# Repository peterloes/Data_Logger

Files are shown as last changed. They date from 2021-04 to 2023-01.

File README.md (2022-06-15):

# Next generation of data logger for varied range support of sensors.

A standalone platform to get environmental impact around organisms (animals).
Enable long-term observations of different selectable sensors (I2C Interfaces).
Two pulse counters are included to get lightbarrier activity.

Authors: Loës P., Kempenaers B.(2021) 

## Main advantages against other data logger:

- Available sensors can be freely combined as required.(Firmware adaption)
- Daily regular synchronisation from date and time with DCF77 radio clock receiver.(Firmware adaption)
- Long battery life with lithium battery. (max.17V)
- SD Card includes configuration file.
- Activation times for sensors (x5) to collect data.

## Hardware Design (first draft) supported:

The following firmware is not reviewed.

- Sensirion: Humidity and Temperature Sensor SHT3x-DIS
- Sensirion: CO₂, Humidity and Temperature Sensor SCD30
- Vishay: Fully Integrated Proximity and Ambient Light Sensor with Infrared Emitter VCNL4040
- Pulse Counter     	 

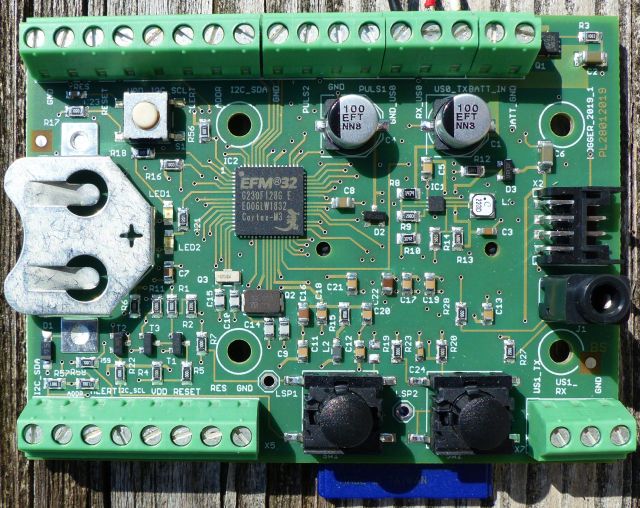
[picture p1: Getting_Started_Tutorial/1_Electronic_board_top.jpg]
My image


Board Dimensions: 80mm x 60mm

Raw data on SD Card:

https://github.com/peterloes/Data_Logger/blob/main/Getting_Started_Tutorial/4_rawdata_BOX0999.TXT

Configuration data on SD Card:

https://github.com/peterloes/Data_Logger/blob/main/Software/CONFIG.TXT

Schematics:

https://github.com/peterloes/Data_Logger/blob/main/Schematics/Logger.sch.pdf

Housing:

https://github.com/peterloes/Data_Logger/blob/main/Getting_Started_Tutorial/11_Electronic_housing.jpg

## Hyperterminal Screens

Shows SHT31X-D (0x45) and SHT31X-D (0x45)

https://github.com/peterloes/Data_Logger/blob/main/Getting_Started_Tutorial/3_Hyperterminal_3.jpg

https://github.com/peterloes/Data_Logger/blob/main/Getting_Started_Tutorial/3_Hyperterminal_4.jpg

In operation with Interval (configuration.txt) : 3,2V@0,54mA

Shows Vishay VCNL4040 (0x60) and SHT31X-D (0x45)

https://github.com/peterloes/Data_Logger/blob/main/Getting_Started_Tutorial/3_Hyperterminal_5.jpg

Shows Vishay VCNL4040 (0x60) and Sensirion SCD30 CO2 (0x61)

https://github.com/peterloes/Data_Logger/blob/main/Getting_Started_Tutorial/3_Hyperterminal_6.jpg

## Board Power

 - Lithium battery  17V/300mA(maximum) e.g. 12,8V 7,5Ah 96Wh 
 - LS14250 Primary Lithium-Thionyl chloride    3.6V/1200mAh 

Sensors can powered by VBATT_1(3.3V), VBATT_2(3V):

 - Sensirion: Humidity and Temperature Sensor SHT3x-DIS:        600µA@3,3V

 - Sensirion: CO₂, Humidity and Temperature Sensor SCD30:     max.75mA@3,3V 

 - Vishay: Proximity Sensor and Ambient Light Sensor VCNL 4040: 300µA@2,5V

   Similar Software(SensorMon.c): https://github.com/peterloes/HRD_SENSOR

Optional components:

https://github.com/peterloes/Clock_receiver_RFID-MS_MOMO_TAMDL

https://github.com/peterloes/Booter_RFID-MS_MOMO_TAMDL

Outlook:

The Data Logger can feature two arrays with different sensors over 25 meters. (sensor-array x 2)

C is the Greenest Programming Language

To achieve its power and energy-efficiency features, EFM32 products utilize ultralow active and idle power,
fast wakeup and processing times, and most important, the ability to intelligently interact with peripherals
and sensors autonomously without waking up the CPU and consuming more power.

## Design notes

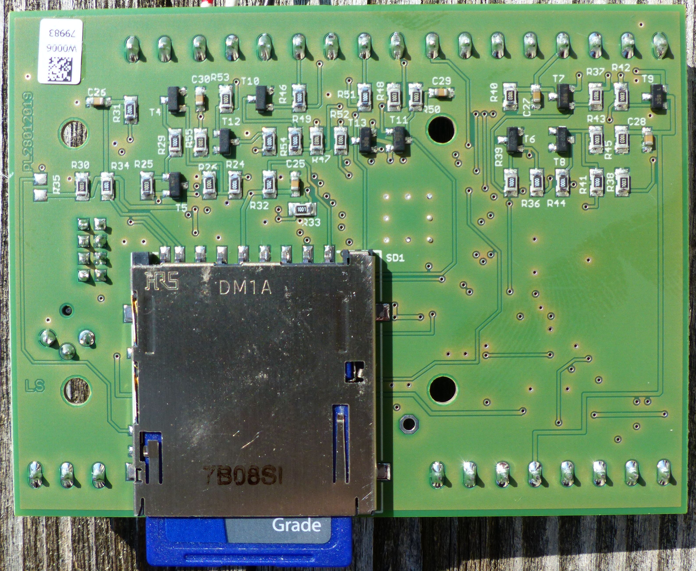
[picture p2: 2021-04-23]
Getting_Started_Tutorial/2_Electronic_board_bottom.jpg

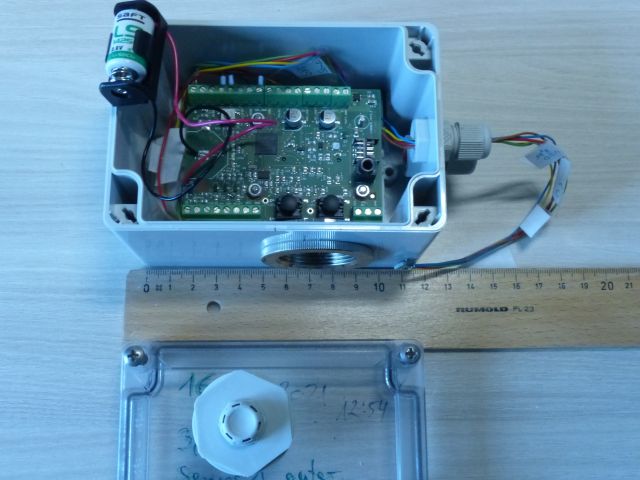
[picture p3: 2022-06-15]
Getting_Started_Tutorial/11_Electronic_housing.jpg

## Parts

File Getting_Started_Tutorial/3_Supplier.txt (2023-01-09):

Lithium Ionen rechargeable battery pack Art.Nr. 60.16294 Panasonic NCR 18650GA 4S2P
14,4Volt 6900mAh inklusive SMBus Kabel je. 150mm 

DYNAMIS Batterien GmbH
Josef Pfeil

Brühlstraße 15  D- 78465 Dettingen / Konstanz
Tel. +49 (0) 75 33/93 669-15
mailto:josef.pfeil@dynamis-batterien.de
www.dynamis-batterien.de

Supplier of all Electronic Boards

Top-Print Electronic GmbH
Oskar Schmid

Rosenheimer Landstr. 129a
85521 Ottobrunn
Germany
Tel.: +49-89-60668047
Fax: +49-89-60668049
mailto: info@top-print.eu
https://www.leiterplatten-muenchen.de/

FTDI Chip cable (3.5mm Audio Jack to USB)
TTL-232R-3V3-AJ

https://de.rs-online.com/
Battery holder with cable
RS PRO Batteriehalter mit Drahtanschluss 1/2 AA Batterien
RS Best.-Nr.: 185-4655

Docklight RS232 Terminal / RS232 Monitor
https://docklight.de/information/

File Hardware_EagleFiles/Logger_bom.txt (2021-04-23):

Stückliste exportiert aus C:/MPIO/TECHNIK/HARDWARE/EAGLE_FILES/Logger_2019/Logger_2019_1.sch am 21.04.2021 15:29

Part  Value                   Device                  Package                Description                                                    MF MPN     OC_FARNELL OC_NEWARK PACKAGE  SUPPLIER         
BH1   KEYSTONE_CELL_CLIP 3082 3082                    3082                                                                                                                                            
C1    100µF/25V               CPOL-EUE                PANASONIC_E            POLARIZED CAPACITOR, European symbol                                                                                     
C2    10µF/25V                C-EUC1206               C1206                  CAPACITOR, European symbol                                                                                               
C3    22µF/10V                C-EUC0603               C0603                  CAPACITOR, European symbol                                                                                               
C4    100µF/25V               CPOL-EUE                PANASONIC_E            POLARIZED CAPACITOR, European symbol                                                                                     
C5    100nF/16V               C-EUC0805               C0805                  CAPACITOR, European symbol                                                                                               
C6    10µ/25V                 C-EUC1206               C1206                  CAPACITOR, European symbol                                                                                               
C7    100n                    C_SMD0805               0805                                                                                                                                            
C8    1u                      C_SMD0805               0805                                                                                                                                            
C9    12p                     C_SMD0805               0805                                                                                                                                            
C10   18p                     C_SMD0805               0805                                                                                                                                            
C11   100n                    C_SMD0805               0805                                                                                                                                            
C12   100n                    C_SMD0805               0805                                                                                                                                            
C13   100n                    C_SMD0805               0805                                                                                                                                            
C14   12p                     C_SMD0805               0805                                                                                                                                            
C15   18p                     C_SMD0805               0805                                                                                                                                            
C16   10µ                     C_SMD0805               0805                                                                                                                                            
C17   100n                    C_SMD0805               0805                                                                                                                                            
C18   100n                    C_SMD0805               0805                                                                                                                                            
C19   100n                    C_SMD0805               0805                                                                                                                                            
C20   100n                    C_SMD0805               0805                                                                                                                                            
C21   100n                    C_SMD0805               0805                                                                                                                                            
C22   10µ                     C_SMD0805               0805                                                                                                                                            
C23   10n                     C-EUC0603               C0603                  CAPACITOR, European symbol                                                                                               
C24   10n                     C-EUC0603K              C0603K                 CAPACITOR, European symbol                                                                                               
C25   100nF                   C-EUC0603               C0603                  CAPACITOR, European symbol                                                                                               
C26   100nF                   C-EUC0603               C0603                  CAPACITOR, European symbol                                                                                               
C27   100nF                   C-EUC0603               C0603                  CAPACITOR, European symbol                                                                                               
C28   100nF                   C-EUC0603               C0603                  CAPACITOR, European symbol                                                                                               
C29   100nF                   C-EUC0603               C0603                  CAPACITOR, European symbol                                                                                               
C30   100nF                   C-EUC0603               C0603                  CAPACITOR, European symbol                                                                                               
D1    RSX101M-30              DIODE-SOD123            SOD123                 DIODE                                                                                                                    
D2    BAT54C                  D2A_SOT23               SOT-23$1               Dual DIODE                                                                                                               
D3    BAT54C                  D2A_SOT23               SOT-23$1               Dual DIODE                                                                                                               
IC1   TPS62125                TPS62125                DSG_PWSO-N8_EXP                                                                                                                                 
IC2   EFM32G230F128           EFM32G230F128           QFN64                  EFM32G230F128 Gecko Microcontroller in 9mm x 9mm QFN64 package                                                           
J1    LUMBERG1502_01          LUMBERG1502_01          LUMBERG1502_01                                                                                                                                  
L1    LPS3008/22µH            LPS3008                 LPS3008                                                                                                                                         
L2    BLM21B102S              WE-CBF-7427920_0805     0805                   SMD EMI Suppression Ferrite Beads WE-CBF                          7427920 1635707    08P2358   IND-0805 Wuerth Elektronik
LED1  SML-H12U8TT86           LEDCHIPLED_0805         CHIPLED_0805           LED                                                                                                                      
LED2  SML-H12Y8TT86           LEDCHIPLED_0805         CHIPLED_0805           LED                                                                                                                      
LSP1  (n.b.)SE13              SE13                    SE13                   SOLDER PAD E1542,  drill 1,3mm, distributor Buerklin, 07F815                                                             
LSP2  (n.b.)SE13              SE13                    SE13                   SOLDER PAD E1542,  drill 1,3mm, distributor Buerklin, 07F815                                                             
PASS1 ROUND_1MM1.5            ROUND_1MM1.5            ROUND2_1.5MM                                                                                                                                    
PASS2 ROUND_1MM1.5            ROUND_1MM1.5            ROUND2_1.5MM                                                                                                                                    
Q1    SI7121DN                TRANSISTOR-FET_SI7113DN TRANSISTOR-FET_1212-8S                                                                                                                          
Q2    NX5032GA/32MHz/8pF      CRYSTAL2P5.0X3.2        CRYSTAL2P5.0X3.2       Quarz Crystal                                                                                                            
Q3    CM7V, 32768Hz/12.5pF    CRYSTAL2P               CRYSTAL2P3.2X1.5       Quarz Crystal                                                                                                            
R1    100                     R-EU_R0805              R0805                  RESISTOR, European symbol                                                                                                
R2    100K                    R-EU_R0805              R0805                  RESISTOR, European symbol                                                                                                
R3    100k                    R-EU_R0805              R0805                  RESISTOR, European symbol                                                                                                
R4    100K                    R-EU_R0805              R0805                  RESISTOR, European symbol                                                                                                
R5    100                     R-EU_R0805              R0805                  RESISTOR, European symbol                                                                                                
R6    100K                    R-EU_R0805              R0805                  RESISTOR, European symbol                                                                                                
R7    100                     R-EU_R0805              R0805                  RESISTOR, European symbol                                                                                                
R8    1M47                    R-EU_R0805              R0805                  RESISTOR, European symbol                                                                                                
R9    200K                    R-EU_R0805              R0805                  RESISTOR, European symbol                                                                                                
R10   30K9                    R-EU_R0805              R0805                  RESISTOR, European symbol                                                                                                
R11   100K                    R-EU_R0805              R0805                  RESISTOR, European symbol                                                                                                
R12   100K                    R-EU_R0805              R0805                  RESISTOR, European symbol                                                                                                
R13   2M                      R-EU_R0805              R0805                  RESISTOR, European symbol                                                                                                
R14   560K                    R-EU_R0805              R0805                  RESISTOR, European symbol                                                                                                
R15   1                       R-EU_R0805              R0805                  RESISTOR, European symbol                                                                                                
R16   100K                    R-EU_R0805              R0805                  RESISTOR, European symbol                                                                                                
R17   100                     R-EU_R0805              R0805                  RESISTOR, European symbol                                                                                                
R18   1K2                     R-EU_R0805              R0805                  RESISTOR, European symbol                                                                                                
R19   (n.b.)100K/*10nF*/      R-EU_R0805              R0805                  RESISTOR, European symbol                                                                                                
R20   100K                    R-EU_R0805              R0805                  RESISTOR, European symbol                                                                                                
R21   1K2                     R-EU_R0805              R0805                  RESISTOR, European symbol                                                                                                
R22   100                     R-EU_R0805              R0805                  RESISTOR, European symbol                                                                                                
R23   100                     R-EU_R0805              R0805                  RESISTOR, European symbol                                                                                                
R24   100                     R-EU_R0805              R0805                  RESISTOR, European symbol                                                                                                
R25   100K                    R-EU_R0805              R0805                  RESISTOR, European symbol                                                                                                
R26   100K                    R-EU_R0805              R0805                  RESISTOR, European symbol                                                                                                
R27   10K                     R-EU_R0805              R0805                  RESISTOR, European symbol                                                                                                
R28   10K                     R-EU_R0805              R0805                  RESISTOR, European symbol                                                                                                
R29   100                     R-EU_R0805              R0805                  RESISTOR, European symbol                                                                                                
R30   100K                    R-EU_R0805              R0805                  RESISTOR, European symbol                                                                                                
R31   10K                     R-EU_R0805              R0805                  RESISTOR, European symbol                                                                                                
R32   10K                     R-EU_R0805              R0805                  RESISTOR, European symbol                                                                                                
R33   1K                      R-EU_R0805              R0805                  RESISTOR, European symbol                                                                                                
R34   1K                      R-EU_R0805              R0805                  RESISTOR, European symbol                                                                                                
R35   (n.b.)10K               R-EU_R0805              R0805                  RESISTOR, European symbol                                                                                                
R36   100                     R-EU_R0805              R0805                  RESISTOR, European symbol                                                                                                
R37   100K                    R-EU_R0805              R0805                  RESISTOR, European symbol                                                                                                
R38   100K                    R-EU_R0805              R0805                  RESISTOR, European symbol                                                                                                
R39   100                     R-EU_R0805              R0805                  RESISTOR, European symbol                                                                                                
R40   100K                    R-EU_R0805              R0805                  RESISTOR, European symbol                                                                                                
R41   100                     R-EU_R0805              R0805                  RESISTOR, European symbol                                                                                                
R42   100K                    R-EU_R0805              R0805                  RESISTOR, European symbol                                                                                                
R43   100K                    R-EU_R0805              R0805                  RESISTOR, European symbol                                                                                                
R44   100                     R-EU_R0805              R0805                  RESISTOR, European symbol                                                                                                
R45   100K                    R-EU_R0805              R0805                  RESISTOR, European symbol                                                                                                
R46   100                     R-EU_R0805              R0805                  RESISTOR, European symbol                                                                                                
R47   100K                    R-EU_R0805              R0805                  RESISTOR, European symbol                                                                                                
R48   100K                    R-EU_R0805              R0805                  RESISTOR, European symbol                                                                                                
R49   100                     R-EU_R0805              R0805                  RESISTOR, European symbol                                                                                                
R50   100K                    R-EU_R0805              R0805                  RESISTOR, European symbol                                                                                                
R51   100                     R-EU_R0805              R0805                  RESISTOR, European symbol                                                                                                
R52   100K                    R-EU_R0805              R0805                  RESISTOR, European symbol                                                                                                
R53   100K                    R-EU_R0805              R0805                  RESISTOR, European symbol                                                                                                
R54   100                     R-EU_R0805              R0805                  RESISTOR, European symbol                                                                                                
R55   100K                    R-EU_R0805              R0805                  RESISTOR, European symbol                                                                                                
R56   1K                      R-EU_R0805              R0805                  RESISTOR, European symbol                                                                                                
R57   1K                      R-EU_R0805              R0805                  RESISTOR, European symbol                                                                                                
R58   1K                      R-EU_R0805              R0805                  RESISTOR, European symbol                                                                                                
R59   1K                      R-EU_R0805              R0805                  RESISTOR, European symbol                                                                                                
S1    SWPB_B3S1000            DTSM-6                  DTSM-6                                                                                                                                          
SD1   DM1AA-SF-PEJ            DM1AA-SF-PEJ            DM1AA-SF-PEJ                                                                                                                                    
SW1   5GSH935                 5GSH935                 MULTIMEC_5GSH935                                                                                                                                
SW2   5GSH935                 5GSH935                 MULTIMEC_5GSH935                                                                                                                                
T1    2N7002                  NMOSSOT23               SOT-23                 MOS FET                                                                   unknown    unknown                             
T2    FDN358P                 ZETEX_PMOSSOT23         ZETEX_SOT-23           MOS FET                                                                                                                  
T3    2N7002                  NMOSSOT23               SOT-23                 MOS FET                                                                   unknown    unknown                             
T4    2N7002                  ZETEX_NMOSSOT23         ZETEX_SOT-23           MOS FET                                                                                                                  
T5    FDN358P                 ZETEX_PMOSSOT23         ZETEX_SOT-23           MOS FET                                                                                                                  
T6    2N7002                  ZETEX_NMOSSOT23         ZETEX_SOT-23           MOS FET                                                                                                                  
T7    FDN358P                 ZETEX_PMOSSOT23         ZETEX_SOT-23           MOS FET                                                                                                                  
T8    2N7002                  ZETEX_NMOSSOT23         ZETEX_SOT-23           MOS FET                                                                                                                  
T9    FDN358P                 ZETEX_PMOSSOT23         ZETEX_SOT-23           MOS FET                                                                                                                  
T10   2N7002                  ZETEX_NMOSSOT23         ZETEX_SOT-23           MOS FET                                                                                                                  
T11   FDN358P                 ZETEX_PMOSSOT23         ZETEX_SOT-23           MOS FET                                                                                                                  
T12   2N7002                  ZETEX_NMOSSOT23         ZETEX_SOT-23           MOS FET                                                                                                                  
T13   FDN358P                 ZETEX_PMOSSOT23         ZETEX_SOT-23           MOS FET                                                                                                                  
X1    MKDS1/2-3,81            MKDS1/2-3,81            2POL381                MKDS 1/2-3,81 - Order No. 1727010 (RS-Online - 101-5384)                                                                 
X2    DF11_8DP_2DS            DP11_8DP_2DS            DP11_8DP-2DS                                                                                                                                    
X3    MKDS1/3-3,81            MKDS1/3-3,81            3POL381                MKDS 1/3-3,81 - Order No. 1727023 (RS-Online - 101-5390)                                                                 
X4    MKDS1/8-3,81            MKDS1/8-3,81            8POL381                MKDS 1/8-3,81 - Order No. 1727078                                                                                        
X5    MKDS1/8-3,81            MKDS1/8-3,81            8POL381                MKDS 1/8-3,81 - Order No. 1727078                                                                                        
X6    MKDS1/4-3,81            MKDS1/4-3,81            4POL381                MKDS 1/4-3,81 - Order No. 1727036                                                                                        
X7    MKDS1/3-3,81            MKDS1/3-3,81            3POL381                MKDS 1/3-3,81 - Order No. 1727023 (RS-Online - 101-5390)

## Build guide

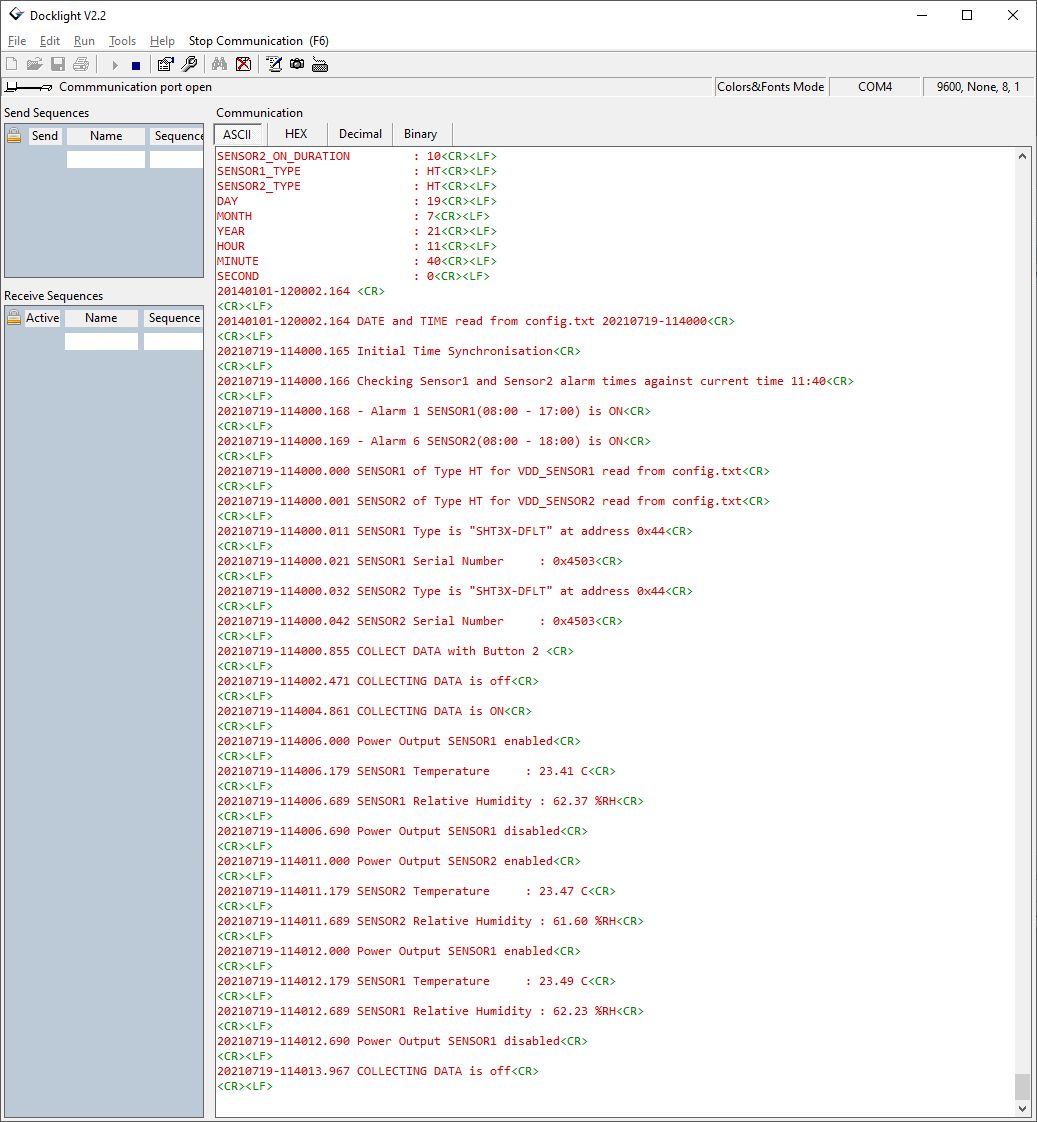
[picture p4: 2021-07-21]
Getting_Started_Tutorial/3_Hyperterminal_4.jpg

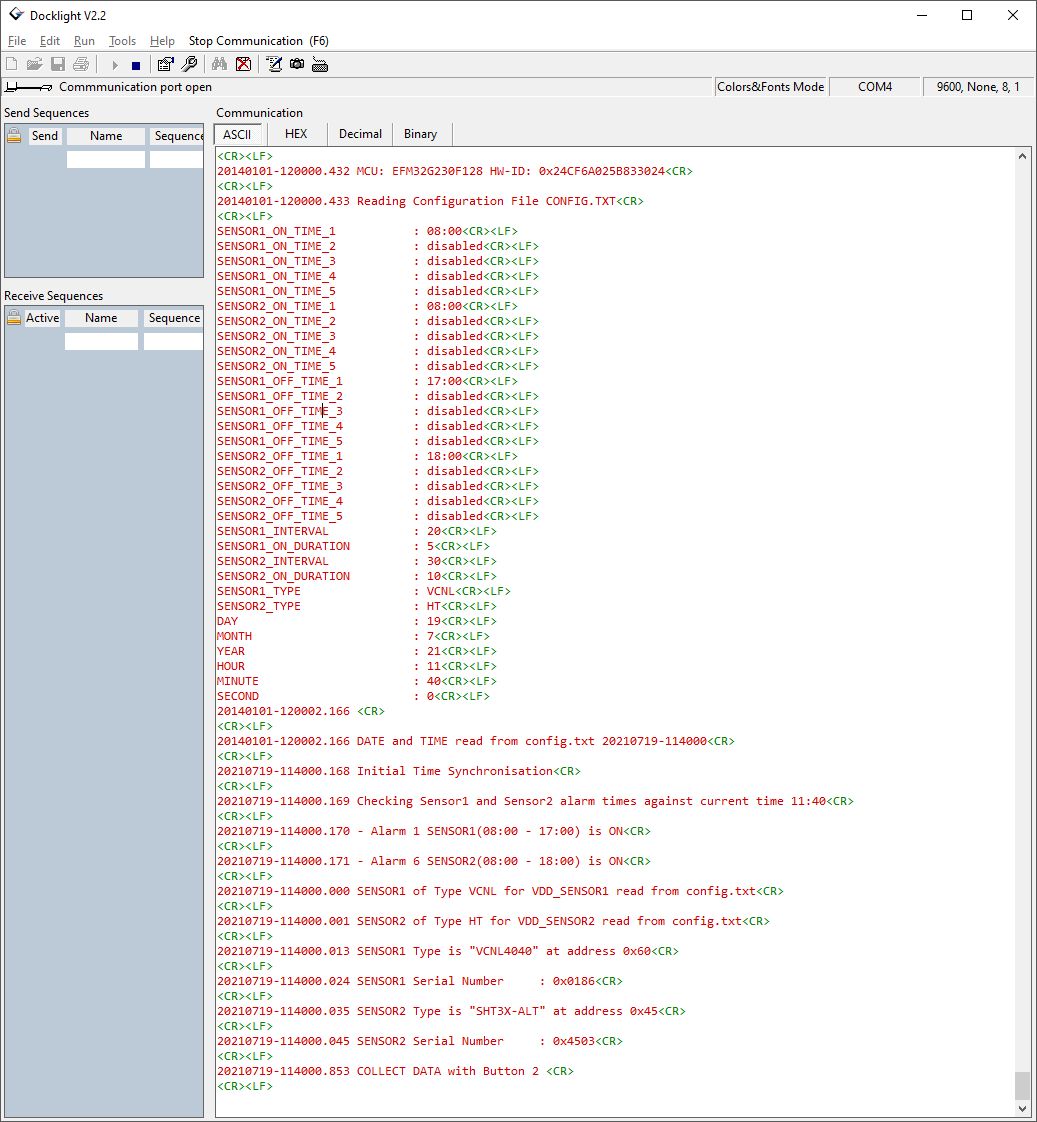
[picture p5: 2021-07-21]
Getting_Started_Tutorial/3_Hyperterminal_5.jpg

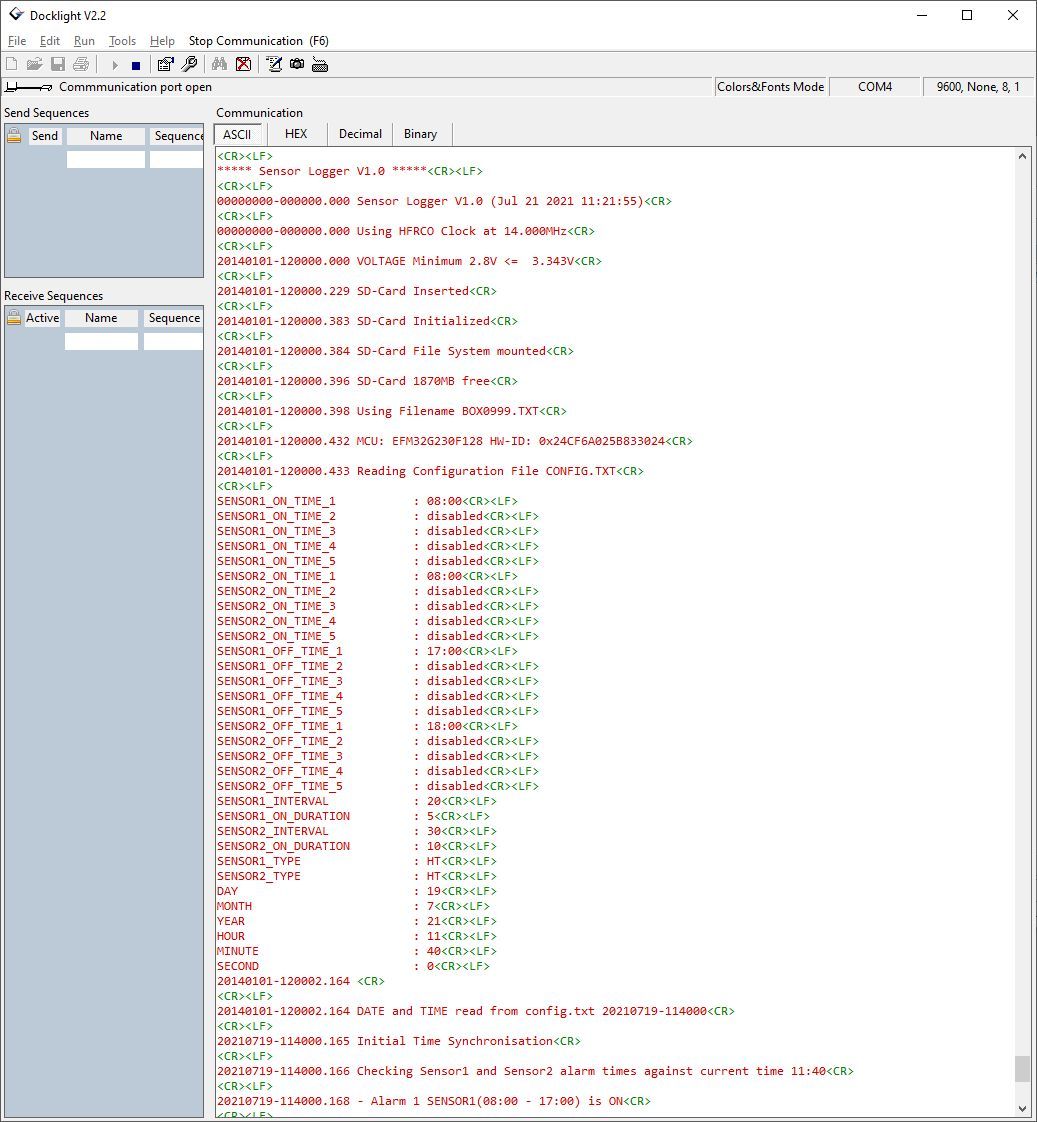
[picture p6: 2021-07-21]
Getting_Started_Tutorial/3_Hyperterminal_3.jpg

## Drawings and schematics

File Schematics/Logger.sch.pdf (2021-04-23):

# EFM32 Power Regulator

## VBATT_1 : 3.3V

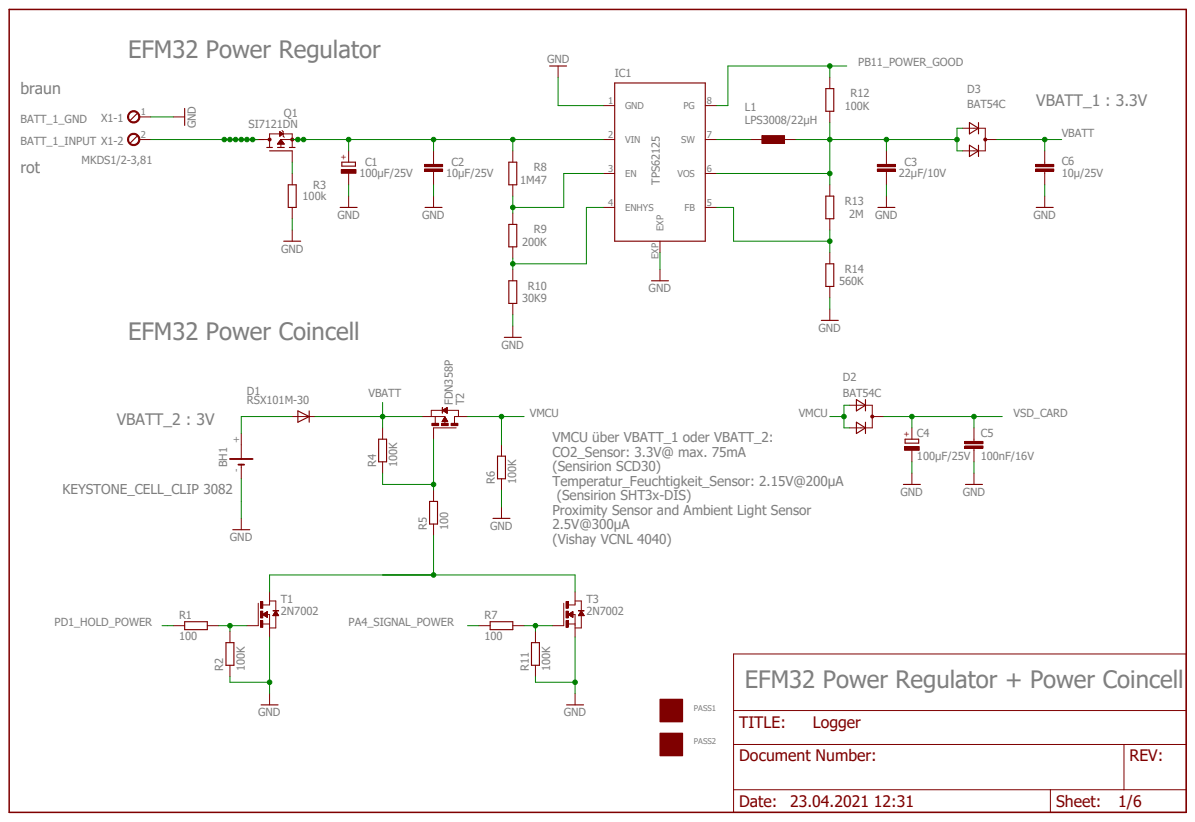
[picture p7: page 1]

EFM32 Power Regulator + Power Coincell

Document Number: | REV:

Date: 23.04.2021 12:31 | Sheet: 1/6

# EFM32 I/O + POWER

## CL f. 32KHz crystal = 22pF as in STK3600

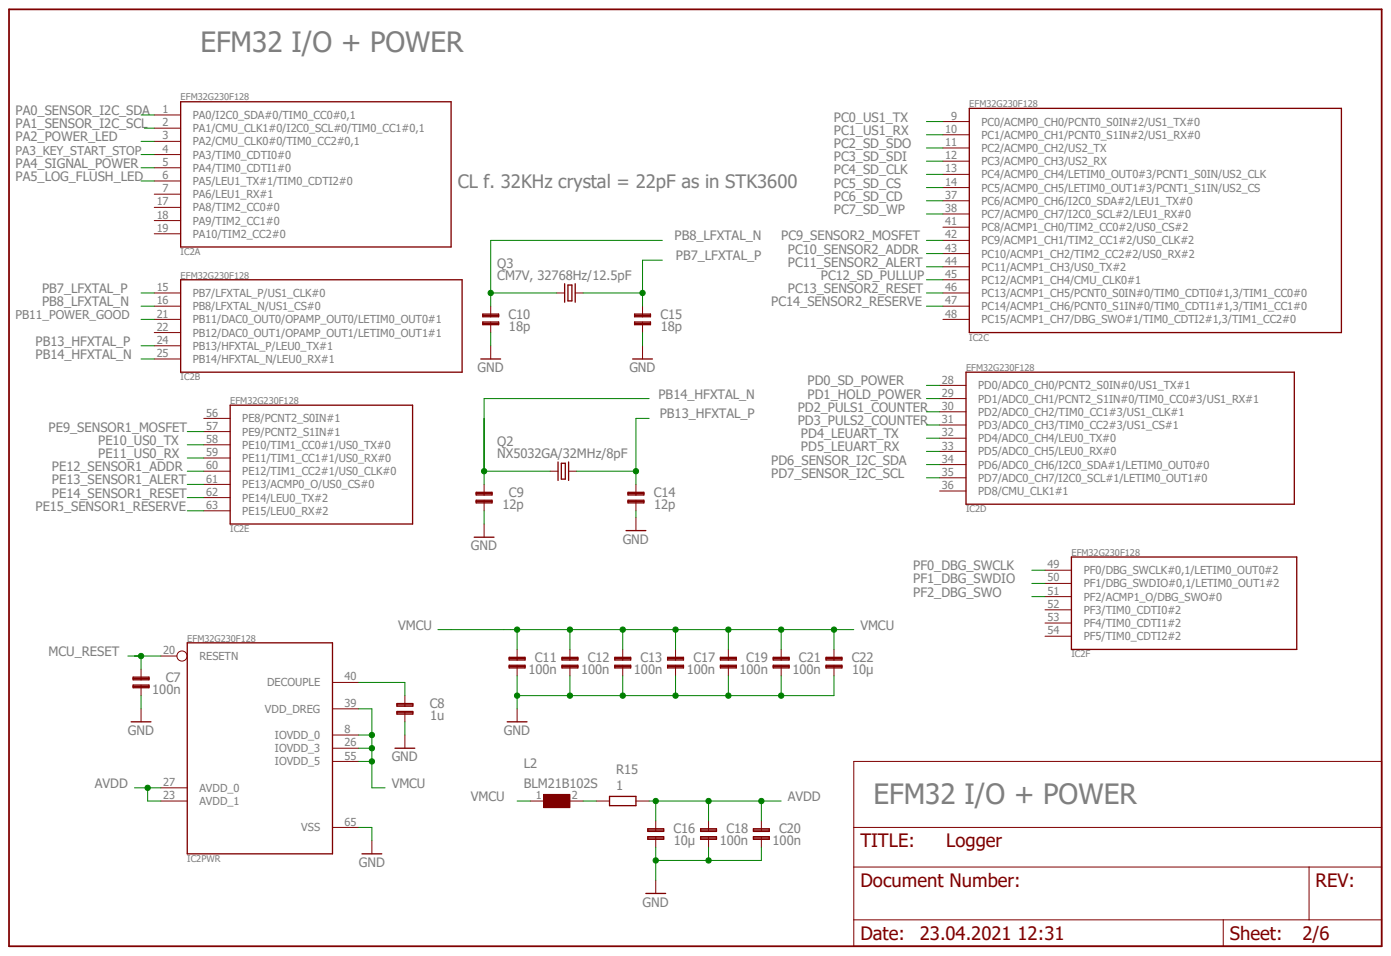
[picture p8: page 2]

Document Number: | REV:

Date: 23.04.2021 12:31 | Sheet: 2/6

DEBUG INTERFACE | LED's

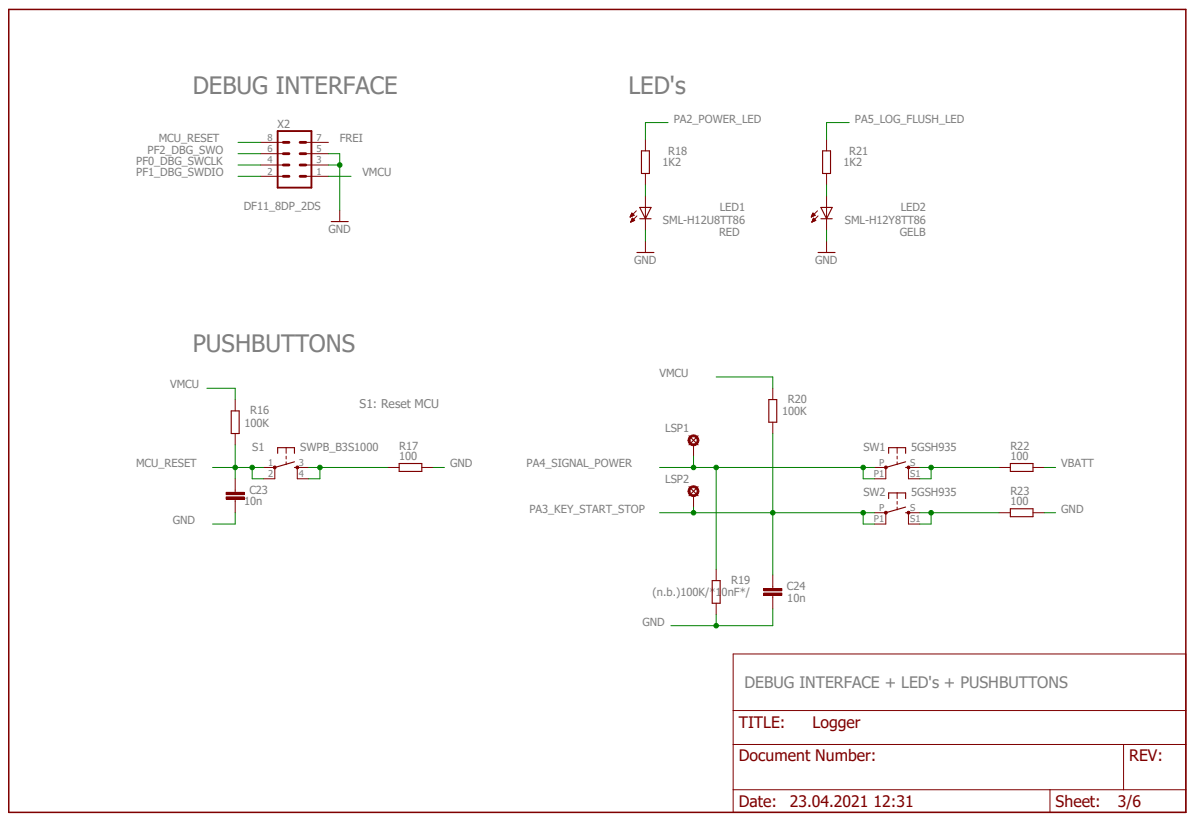
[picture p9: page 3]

DEBUG INTERFACE + LED's + PUSHBUTTONS

Document Number: | REV:

Date: 23.04.2021 12:31 | Sheet: 3/6

# SD SOCKET

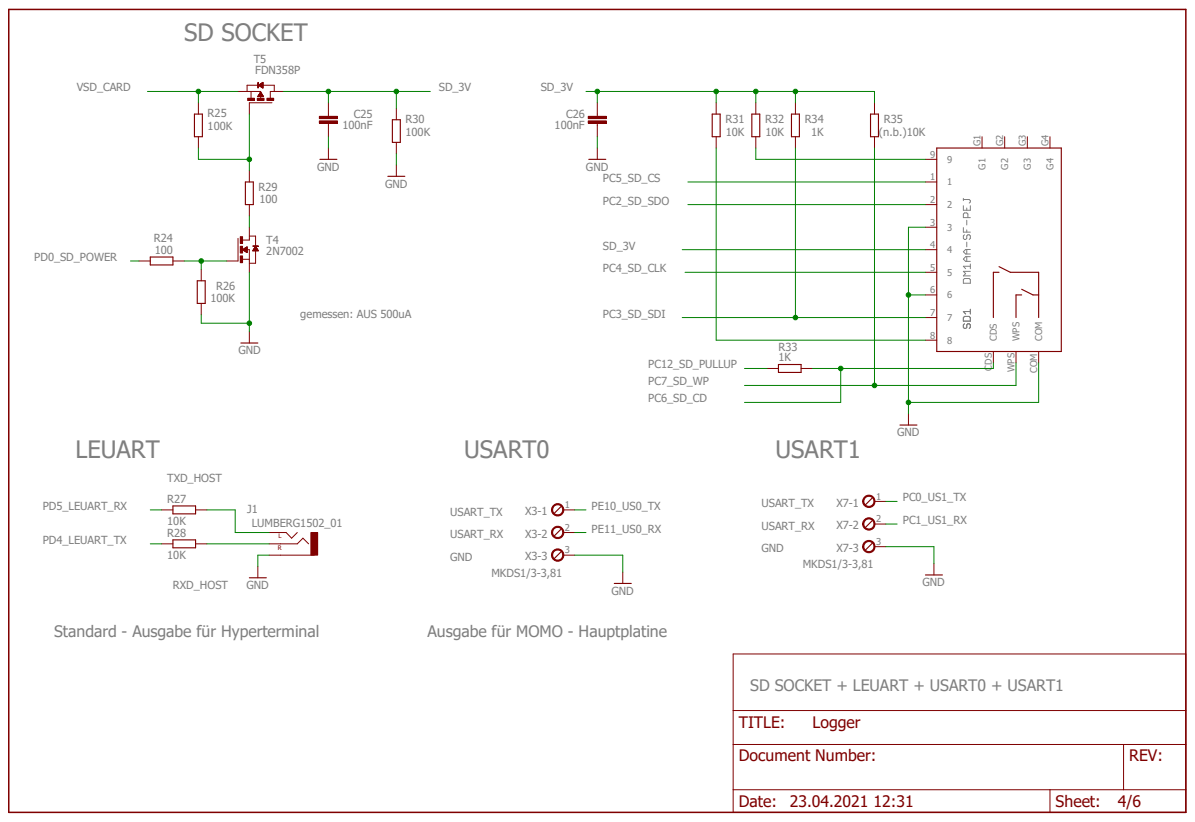
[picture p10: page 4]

Document Number: | REV:

Date: 23.04.2021 12:31 | Sheet: 4/6

# SENSOR_ON_OFF

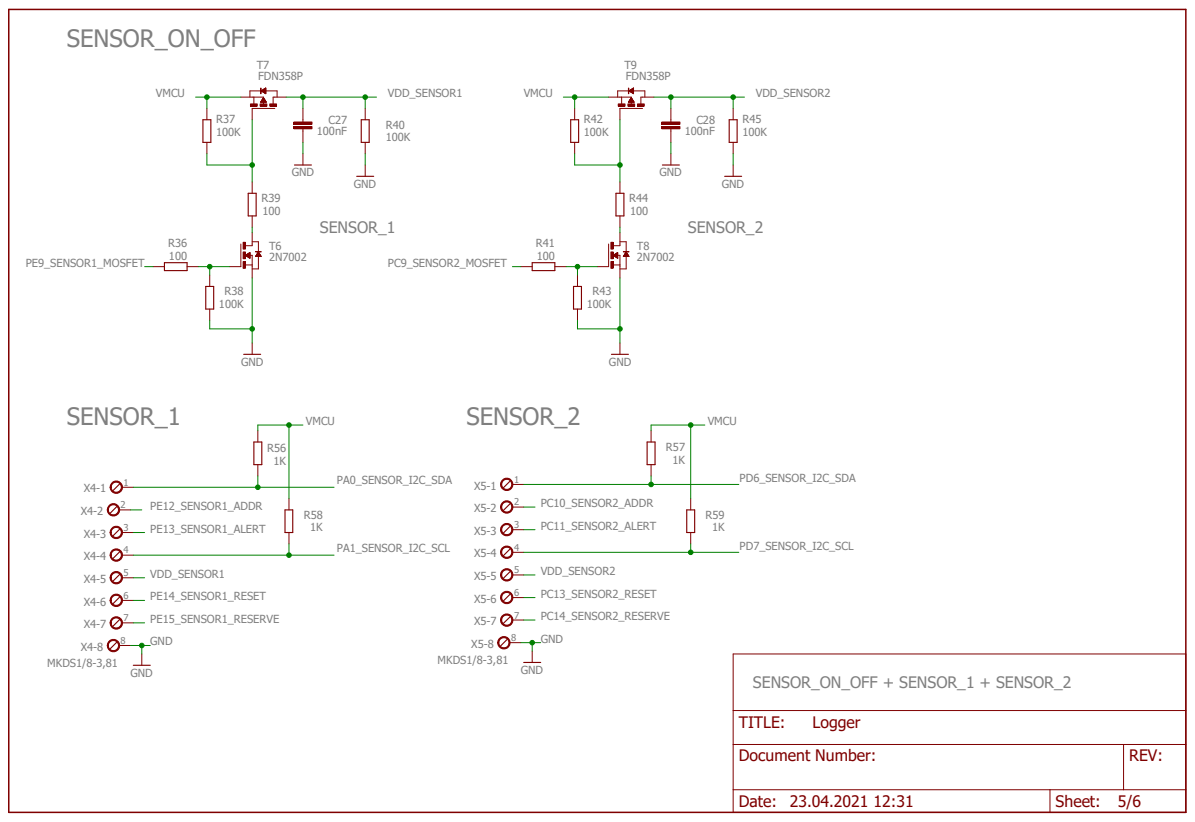
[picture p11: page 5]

Document Number: | REV:

Date: 23.04.2021 12:31 | Sheet: 5/6

# PULS_COUNTER

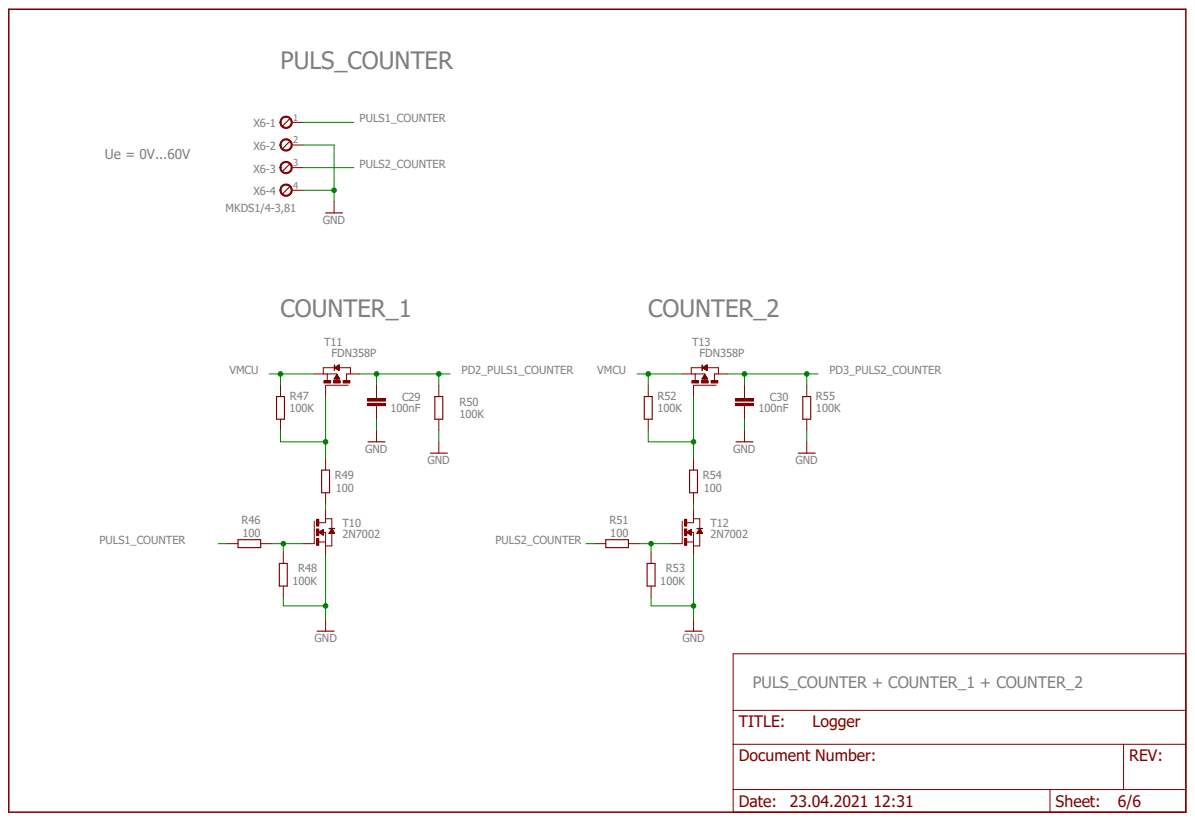
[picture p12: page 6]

Document Number: | REV:

Date: 23.04.2021 12:31 | Sheet: 6/6

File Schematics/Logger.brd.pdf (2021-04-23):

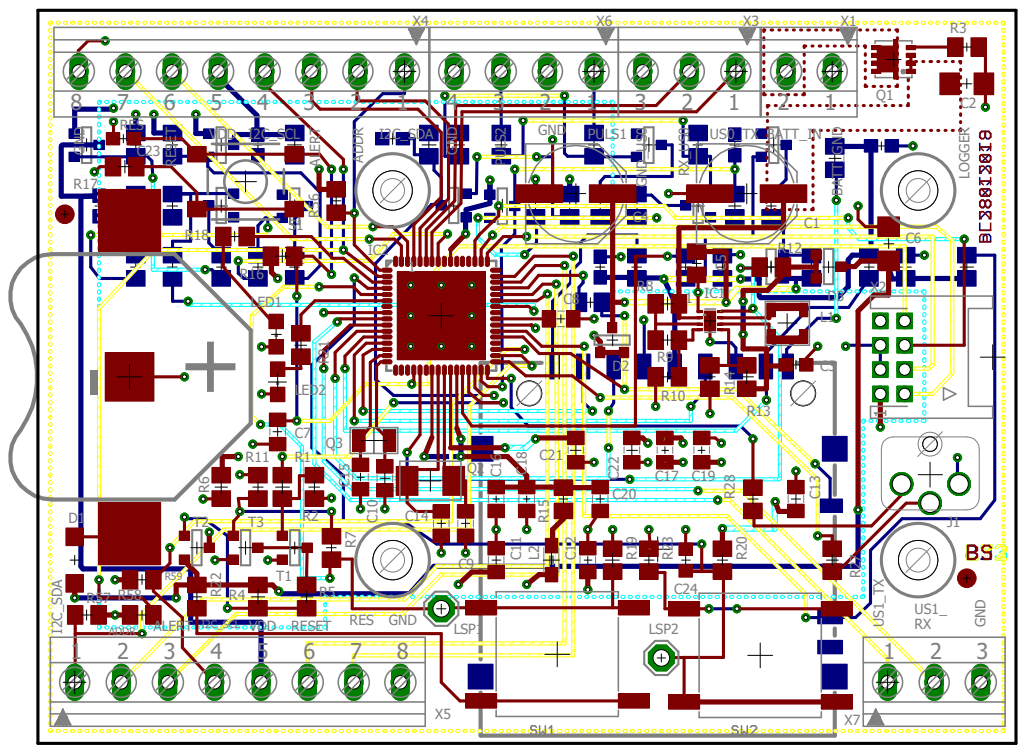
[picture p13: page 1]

I2C_SDA ADDR ALERT I2C_SCL VDD RESET US1_TX US1_ RX GND

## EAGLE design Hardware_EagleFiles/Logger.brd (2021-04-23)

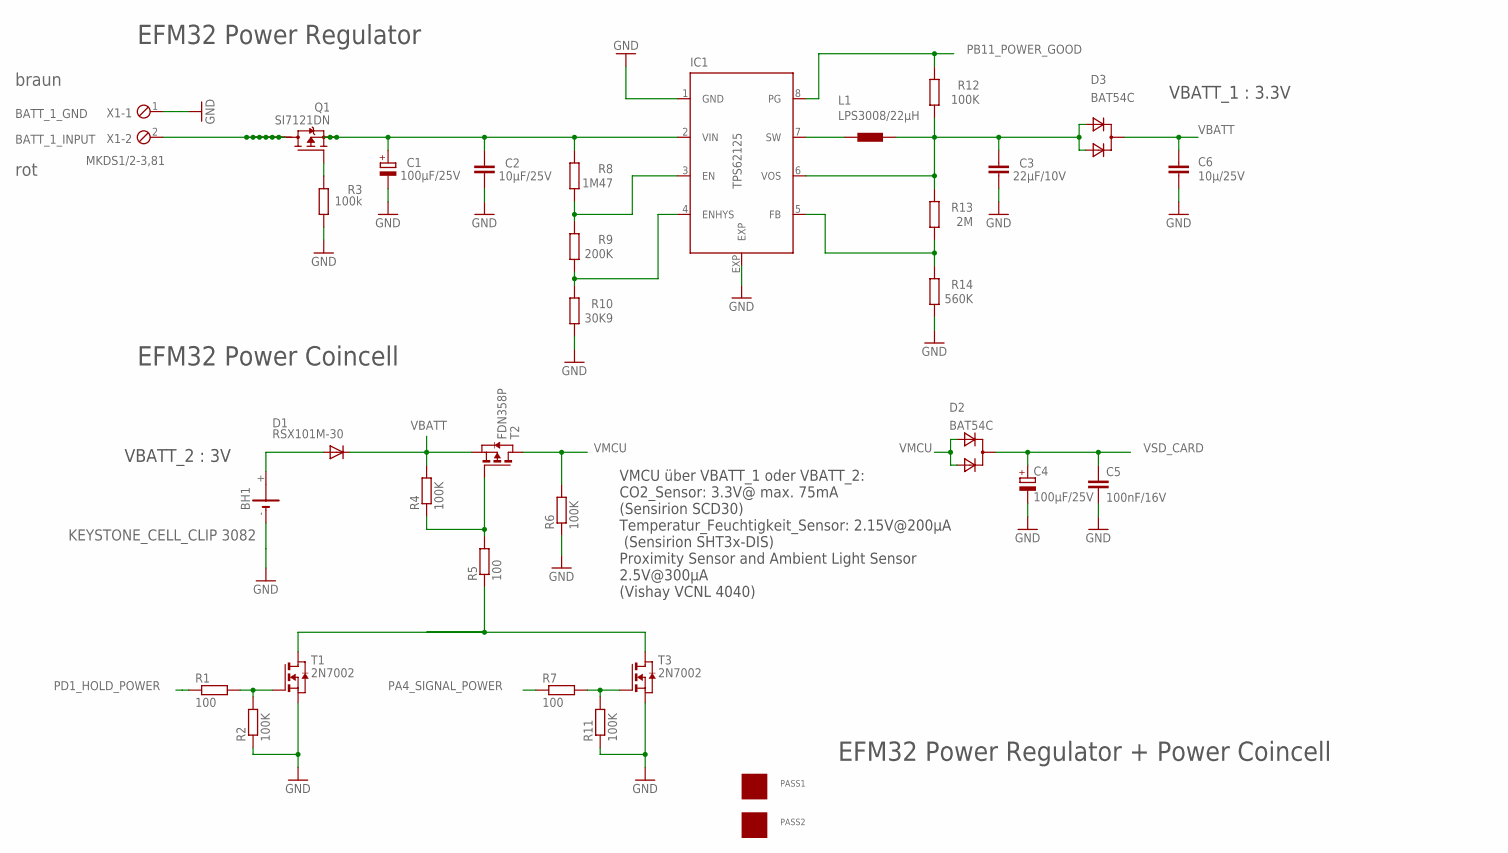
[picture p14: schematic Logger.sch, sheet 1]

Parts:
BH1: KEYSTONE_CELL_CLIP 3082; 3082
C1, C4: 100µF/25V; PANASONIC_E
C2: 10µF/25V; C1206
C3: 22µF/10V; C0603
C5: 100nF/16V; C0805
C6: 10µ/25V; C1206
D1: RSX101M-30; SOD123
D2, D3: BAT54C; SOT-23$1
IC1: TPS62125; DSG_PWSO-N8_EXP
L1: LPS3008/22µH; LPS3008
PASS1, PASS2: ROUND_1MM1.5; ROUND2_1.5MM
Q1: SI7121DN; TRANSISTOR-FET_1212-8S
R1, R5, R7: 100; R0805
R2, R4, R6, R11, R12: 100K; R0805
R3: 100k; R0805
R8: 1M47; R0805
R9: 200K; R0805
R10: 30K9; R0805
R13: 2M; R0805
R14: 560K; R0805
T1, T3: 2N7002; SOT-23
T2: FDN358P; ZETEX_SOT-23
X1: MKDS1/2-3,81; 2POL381

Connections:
1: C3.1, D3.2 (A1), D3.3 (A2), IC1.6 (VOS), L1.2, R12.1, R13.2
BATT_INPUT: C1.+, C2.1, IC1.2 (VIN), Q1.1 (S), Q1.2 (S), Q1.3 (S), R8.2
GND: BH1.-, C1.-, C2.2, C3.2, C4.-, C5.2, C6.1, IC1.1 (GND), IC1.EXP, R2.1, R3.1, R6.1, R10.1, R11.1, R14.1, T1.2 (S), T3.2 (S), X1.1; also elsewhere on the board
unnamed: R1.2, R2.2, T1.3 (G)
unnamed: IC1.3 (EN), R8.1, R9.2
unnamed: IC1.4 (ENHYS), R9.1, R10.2
unnamed: IC1.7 (SW), L1.1
unnamed: BH1.+, D1.A
unnamed: Q1.4 (G), R3.2
unnamed: R4.1, R5.2, T2.3 (G)
unnamed: R7.2, R11.2, T3.3 (G)
unnamed: R5.1, T1.1 (D), T3.1 (D)
unnamed: IC1.5 (FB), R13.1, R14.2
PA4_SIGNAL_POWER: R7.1; also elsewhere on the board
PB11_POWER_GOOD: IC1.8 (PG), R12.2; also elsewhere on the board
PD1_HOLD_POWER: R1.1; also elsewhere on the board
VBATT: C6.2, D1.C, D3.1 (C), R4.2, T2.2 (S); also elsewhere on the board
VMCU: D2.2 (A1), D2.3 (A2), R6.2, T2.1 (D); also elsewhere on the board
VSD_CARD: C4.+, C5.1, D2.1 (C); also elsewhere on the board
_: Q1.5 (D), Q1.6 (D), Q1.7 (D), Q1.8 (D), Q1.9 (D), Q1.10 (D), Q1.11 (D), X1.2

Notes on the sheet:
BATT_1_GND
BATT_1_INPUT
EFM32 Power Regulator + Power Coincell
EFM32 Power Regulator
VBATT_1 : 3.3V
braun
rot
EFM32 Power Coincell
VBATT_2 : 3V
VMCU über VBATT_1 oder VBATT_2: CO2_Sensor: 3.3V@ max. 75mA (Sensirion SCD30) Temperatur_Feuchtigkeit_Sensor: 2.15V@200µA (Sensirion SHT3x-DIS) Proximity Sensor and Ambient Light Sensor 2.5V@300µA (Vishay VCNL 4040)

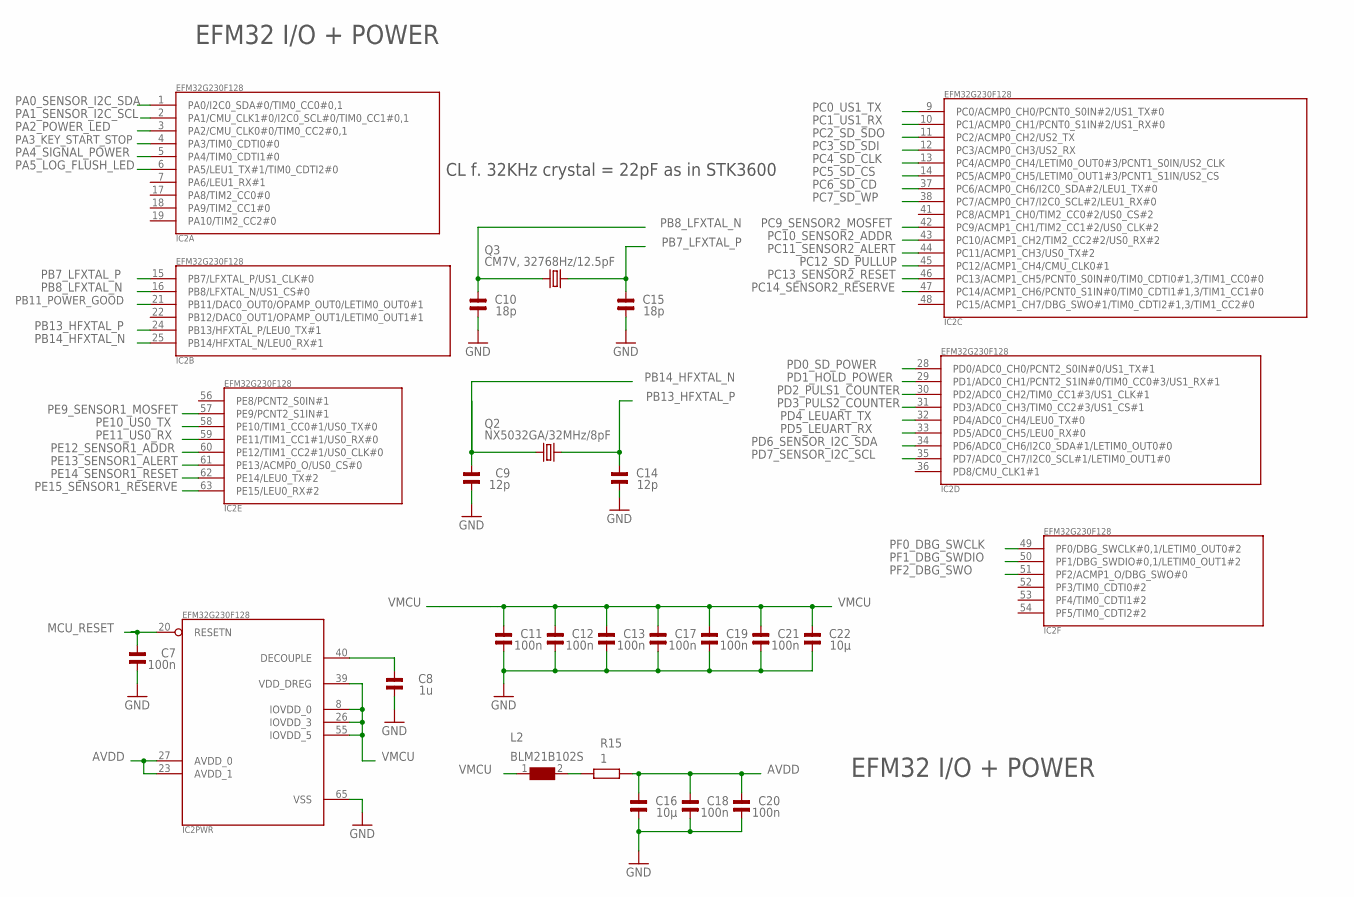
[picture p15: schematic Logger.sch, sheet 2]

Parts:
C7, C11, C12, C13, C17, C18, C19, C20, C21: 100n; 0805
C8: 1u; 0805
C9, C14: 12p; 0805
C10, C15: 18p; 0805
C16, C22: 10µ; 0805
IC2: EFM32G230F128; QFN64
L2: BLM21B102S; 0805
Q2: NX5032GA/32MHz/8pF; CRYSTAL2P5.0X3.2
Q3: CM7V, 32768Hz/12.5pF; CRYSTAL2P3.2X1.5
R15: 1; R0805

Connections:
AVDD: C16.2, C18.2, C20.2, IC2.23 (AVDD_1), IC2.27 (AVDD_0), R15.2
GND: C7.1, C8.1, C9.1, C10.1, C11.1, C12.1, C13.1, C14.1, C15.1, C16.1, C17.1, C18.1, C19.1, C20.1, C21.1, C22.1, IC2.65 (VSS); also elsewhere on the board
MCU_RESET: C7.2, IC2.20 (RESETN); also elsewhere on the board
unnamed: L2.2, R15.1
unnamed: C8.2, IC2.40 (DECOUPLE)
PA0_SENSOR_I2C_SDA: IC2.1 (PA0/I2C0_SDA#0/TIM0_CC0#0,1); also elsewhere on the board
PA1_SENSOR_I2C_SCL: IC2.2 (PA1/CMU_CLK1#0/I2C0_SCL#0/TIM0_CC1#0,1); also elsewhere on the board
PA2_POWER_LED: IC2.3 (PA2/CMU_CLK0#0/TIM0_CC2#0,1); also elsewhere on the board
PA3_KEY_START_STOP: IC2.4 (PA3/TIM0_CDTI0#0); also elsewhere on the board
PA4_SIGNAL_POWER: IC2.5 (PA4/TIM0_CDTI1#0); also elsewhere on the board
PA5_LOG_FLUSH_LED: IC2.6 (PA5/LEU1_TX#1/TIM0_CDTI2#0); also elsewhere on the board
PB7_LFXTAL_P: C15.2, IC2.15 (PB7/LFXTAL_P/US1_CLK#0), Q3.2
PB8_LFXTAL_N: C10.2, IC2.16 (PB8/LFXTAL_N/US1_CS#0), Q3.1
PB11_POWER_GOOD: IC2.21 (PB11/DAC0_OUT0/OPAMP_OUT0/LETIM0_OUT0#1); also elsewhere on the board
PB13_HFXTAL_P: C14.2, IC2.24 (PB13/HFXTAL_P/LEU0_TX#1), Q2.2
PB14_HFXTAL_N: C9.2, IC2.25 (PB14/HFXTAL_N/LEU0_RX#1), Q2.1
PC0_US1_TX: IC2.9 (PC0/ACMP0_CH0/PCNT0_S0IN#2/US1_TX#0); also elsewhere on the board
PC1_US1_RX: IC2.10 (PC1/ACMP0_CH1/PCNT0_S1IN#2/US1_RX#0); also elsewhere on the board
PC2_SD_SDO: IC2.11 (PC2/ACMP0_CH2/US2_TX); also elsewhere on the board
PC3_SD_SDI: IC2.12 (PC3/ACMP0_CH3/US2_RX); also elsewhere on the board
PC4_SD_CLK: IC2.13 (PC4/ACMP0_CH4/LETIM0_OUT0#3/PCNT1_S0IN/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); also elsewhere on the board
PC5_SD_CS: IC2.14 (PC5/ACMP0_CH5/LETIM0_OUT1#3/PCNT1_S1IN/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); also elsewhere on the board
PC6_SD_CD: IC2.37 (PC6/ACMP0_CH6/I2C0_SDA#2/LEU1_TX#0); also elsewhere on the board
PC7_SD_WP: IC2.38 (PC7/ACMP0_CH7/I2C0_SCL#2/LEU1_RX#0); also elsewhere on the board
PC9_SENSOR2_MOSFET: IC2.42 (PC9/ACMP1_CH1/TIM2_CC1#2/US0_CLK#2); also elsewhere on the board
PC10_SENSOR2_ADDR: IC2.43 (PC10/ACMP1_CH2/TIM2_CC2#2/US0_RX#2); also elsewhere on the board
PC11_SENSOR2_ALERT: IC2.44 (PC11/ACMP1_CH3/US0_TX#2); also elsewhere on the board
PC12_SD_PULLUP: IC2.45 (PC12/ACMP1_CH4/CMU_CLK0#1); also elsewhere on the board
PC13_SENSOR2_RESET: IC2.46 (PC13/ACMP1_CH5/PCNT0_S0IN#0/TIM0_CDTI0#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); also elsewhere on the board
PC14_SENSOR2_RESERVE: IC2.47 (PC14/ACMP1_CH6/PCNT0_S1IN#0/TIM0_CDTI1#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); also elsewhere on the board
PD0_SD_POWER: IC2.28 (PD0/ADC0_CH0/PCNT2_S0IN#0/US1_TX#1); also elsewhere on the board
PD1_HOLD_POWER: IC2.29 (PD1/ADC0_CH1/PCNT2_S1IN#0/TIM0_CC0#3/US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); also elsewhere on the board
PD2_PULS1_COUNTER: IC2.30 (PD2/ADC0_CH2/TIM0_CC1#3/US1_CLK#1); also elsewhere on the board
PD3_PULS2_COUNTER: IC2.31 (PD3/ADC0_CH3/TIM0_CC2#3/US1_CS#1); also elsewhere on the board
PD4_LEUART_TX: IC2.32 (PD4/ADC0_CH4/LEU0_TX#0); also elsewhere on the board
PD5_LEUART_RX: IC2.33 (PD5/ADC0_CH5/LEU0_RX#0); also elsewhere on the board
PD6_SENSOR_I2C_SDA: IC2.34 (PD6/ADC0_CH6/I2C0_SDA#1/LETIM0_OUT0#0); also elsewhere on the board
PD7_SENSOR_I2C_SCL: IC2.35 (PD7/ADC0_CH7/I2C0_SCL#1/LETIM0_OUT1#0); also elsewhere on the board
PE9_SENSOR1_MOSFET: IC2.57 (PE9/PCNT2_S1IN#1); also elsewhere on the board
PE10_US0_TX: IC2.58 (PE10/TIM1_CC0#1/US0_TX#0); also elsewhere on the board
PE11_US0_RX: IC2.59 (PE11/TIM1_CC1#1/US0_RX#0); also elsewhere on the board
PE12_SENSOR1_ADDR: IC2.60 (PE12/TIM1_CC2#1/US0_CLK#0); also elsewhere on the board
PE13_SENSOR1_ALERT: IC2.61 (PE13/ACMP0_O/US0_CS#0); also elsewhere on the board
PE14_SENSOR1_RESET: IC2.62 (PE14/LEU0_TX#2); also elsewhere on the board
PE15_SENSOR1_RESERVE: IC2.63 (PE15/LEU0_RX#2); also elsewhere on the board
PF0_DBG_SWCLK: IC2.49 (PF0/DBG_SWCLK#0,1/LETIM0_OUT0#2); also elsewhere on the board
PF1_DBG_SWDIO: IC2.50 (PF1/DBG_SWDIO#0,1/LETIM0_OUT1#2); also elsewhere on the board
PF2_DBG_SWO: IC2.51 (PF2/ACMP1_O/DBG_SWO#0); also elsewhere on the board
VMCU: C11.2, C12.2, C13.2, C17.2, C19.2, C21.2, C22.2, IC2.8 (IOVDD_0), IC2.26 (IOVDD_3), IC2.39 (VDD_DREG), IC2.55 (IOVDD_5), L2.1; also elsewhere on the board

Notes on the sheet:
EFM32 I/O + POWER
CL f. 32KHz crystal = 22pF as in STK3600

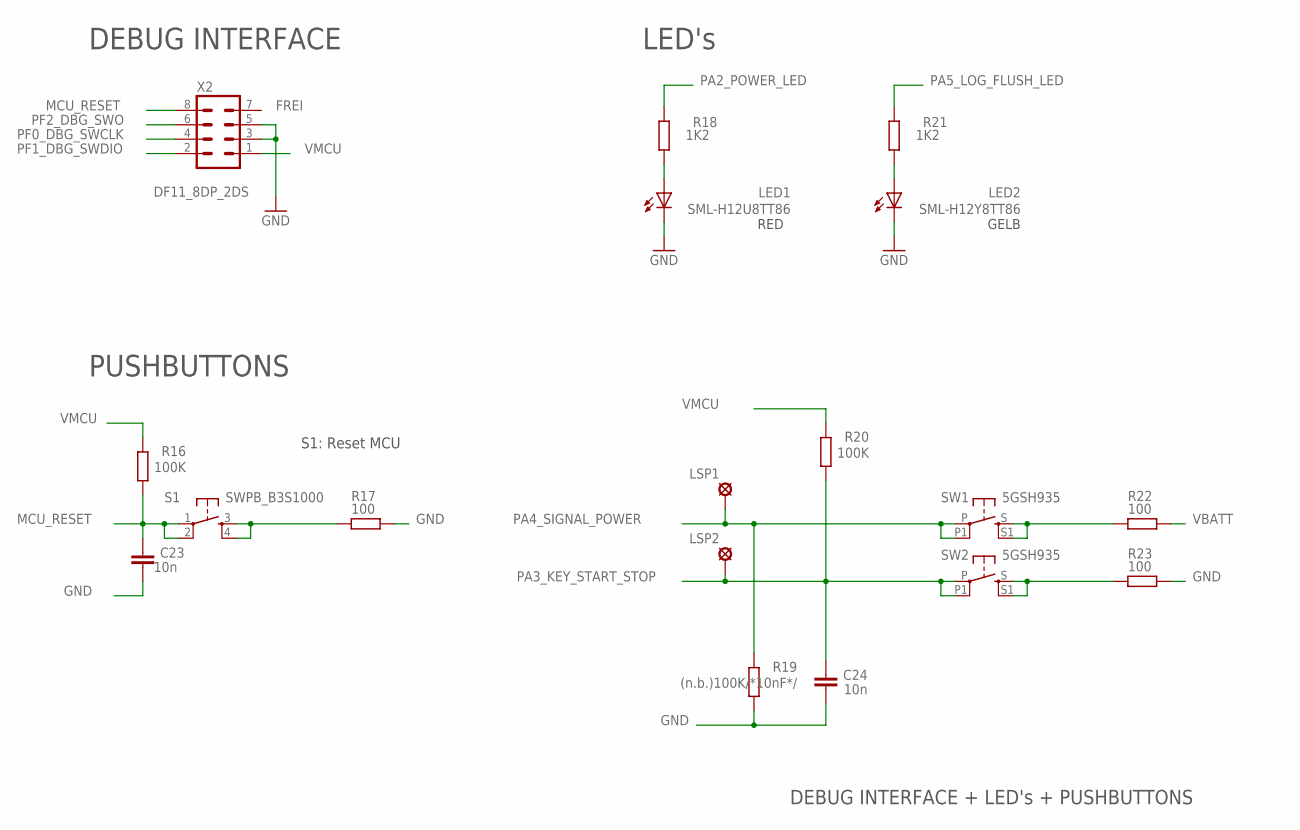
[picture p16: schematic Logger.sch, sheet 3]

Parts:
C23: 10n; C0603
C24: 10n; C0603K
LED1: SML-H12U8TT86; CHIPLED_0805
LED2: SML-H12Y8TT86; CHIPLED_0805
LSP1, LSP2: (n.b.)SE13; SE13
R16, R20: 100K; R0805
R17, R22, R23: 100; R0805
R18, R21: 1K2; R0805
R19: (n.b.)100K/*10nF*/; R0805
S1: SWPB_B3S1000; DTSM-6
SW1, SW2: 5GSH935; MULTIMEC_5GSH935
X2: DF11_8DP_2DS; DP11_8DP-2DS

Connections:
GND: C23.1, C24.1, LED1.C, LED2.C, R17.2, R19.1, R23.2, X2.3, X2.5; also elsewhere on the board
MCU_RESET: C23.2, R16.1, S1.1, S1.2, X2.8; also elsewhere on the board
unnamed: LED1.A, R18.2
unnamed: LED2.A, R21.2
unnamed: R17.1, S1.3, S1.4
unnamed: R23.1, SW2.S, SW2.S1
unnamed: R22.1, SW1.S, SW1.S1
PA2_POWER_LED: R18.1; also elsewhere on the board
PA3_KEY_START_STOP: C24.2, LSP2.MP, R20.1, SW2.P, SW2.P1; also elsewhere on the board
PA4_SIGNAL_POWER: LSP1.MP, R19.2, SW1.P, SW1.P1; also elsewhere on the board
PA5_LOG_FLUSH_LED: R21.1; also elsewhere on the board
PF0_DBG_SWCLK: X2.4; also elsewhere on the board
PF1_DBG_SWDIO: X2.2; also elsewhere on the board
PF2_DBG_SWO: X2.6; also elsewhere on the board
VBATT: R22.2; also elsewhere on the board
VMCU: R16.2, R20.2, X2.1; also elsewhere on the board

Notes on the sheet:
DEBUG INTERFACE + LED's + PUSHBUTTONS
DEBUG INTERFACE
LED's
FREI
GELB
PUSHBUTTONS
S1: Reset MCU
RED

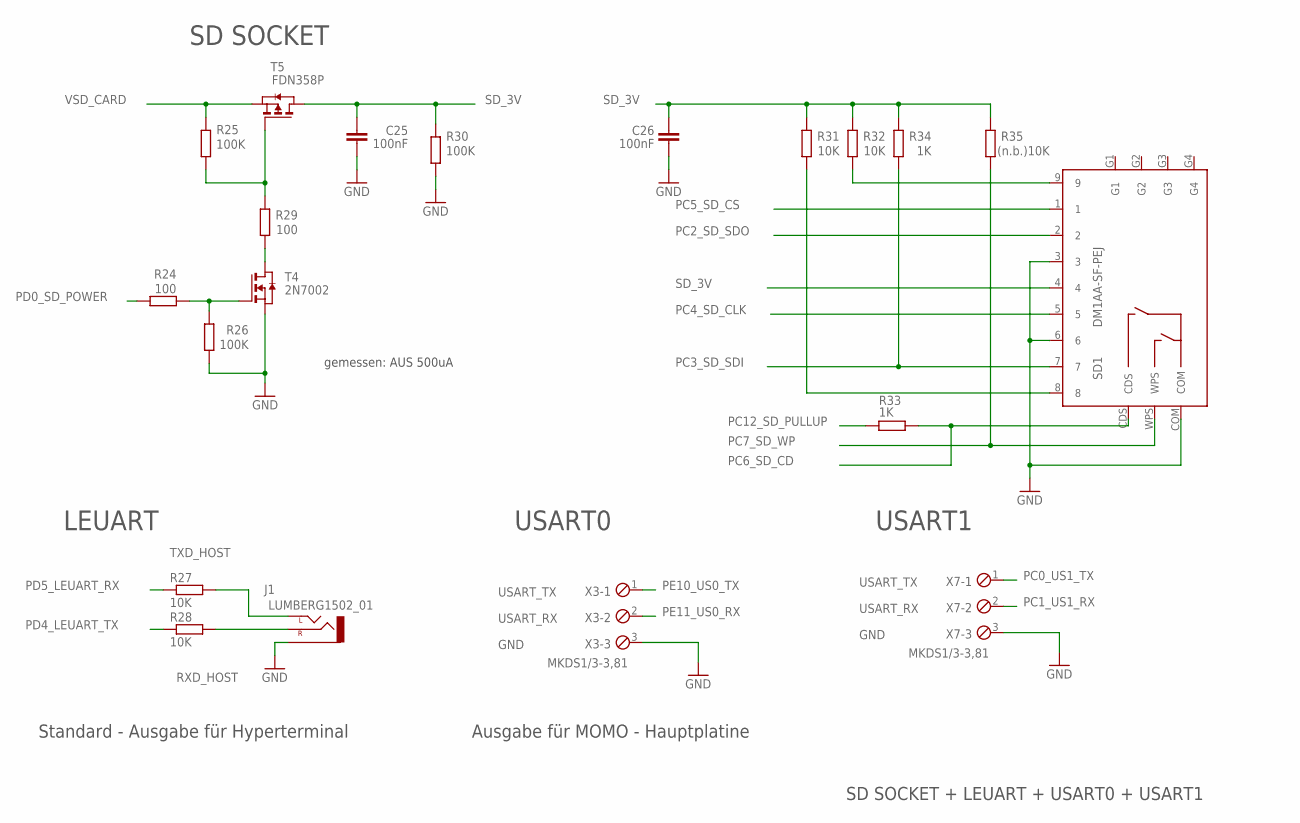
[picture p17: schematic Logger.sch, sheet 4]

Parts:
C25, C26: 100nF; C0603
J1: LUMBERG1502_01
R24, R29: 100; R0805
R25, R26, R30: 100K; R0805
R27, R28, R31, R32: 10K; R0805
R33, R34: 1K; R0805
R35: (n.b.)10K; R0805
SD1: DM1AA-SF-PEJ
T4: 2N7002; ZETEX_SOT-23
T5: FDN358P; ZETEX_SOT-23
X3, X7: MKDS1/3-3,81; 3POL381

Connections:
GND: C25.2, C26.2, J1.P$1 (1-SLEEVE), R26.1, R30.1, SD1.3, SD1.6, SD1.COM, T4.2 (S), X3.3, X7.3; also elsewhere on the board
unnamed: R25.1, R29.2, T5.3 (G)
unnamed: R29.1, T4.1 (D)
unnamed: R24.1, R26.2, T4.3 (G)
unnamed: R32.1, SD1.9
unnamed: R31.1, SD1.8
PC0_US1_TX: X7.1; also elsewhere on the board
PC1_US1_RX: X7.2; also elsewhere on the board
PC2_SD_SDO: SD1.2; also elsewhere on the board
PC3_SD_SDI: R34.1, SD1.7; also elsewhere on the board
PC4_SD_CLK: SD1.5; also elsewhere on the board
PC5_SD_CS: SD1.1; also elsewhere on the board
PC6_SD_CD: R33.1, SD1.CDS; also elsewhere on the board
PC7_SD_WP: R35.1, SD1.WPS; also elsewhere on the board
PC12_SD_PULLUP: R33.2; also elsewhere on the board
PD0_SD_POWER: R24.2; also elsewhere on the board
PD4_LEUART_TX: R28.1; also elsewhere on the board
PD5_LEUART_RX: R27.1; also elsewhere on the board
PE10_US0_TX: X3.1; also elsewhere on the board
PE11_US0_RX: X3.2; also elsewhere on the board
RXD_HOST: J1.P$3 (3-RIGHT), R28.2
SD_3V: C25.1, C26.1, R30.2, R31.2, R32.2, R34.2, R35.2, SD1.4, T5.1 (D)
TXD_HOST: J1.P$2 (2-LEFT), R27.2
VSD_CARD: R25.2, T5.2 (S); also elsewhere on the board

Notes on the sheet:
SD SOCKET + LEUART + USART0 + USART1
LEUART
gemessen: AUS 500uA
SD SOCKET
USART_TX
USART_RX
GND
USART0
Standard - Ausgabe für Hyperterminal
Ausgabe für MOMO - Hauptplatine
USART1

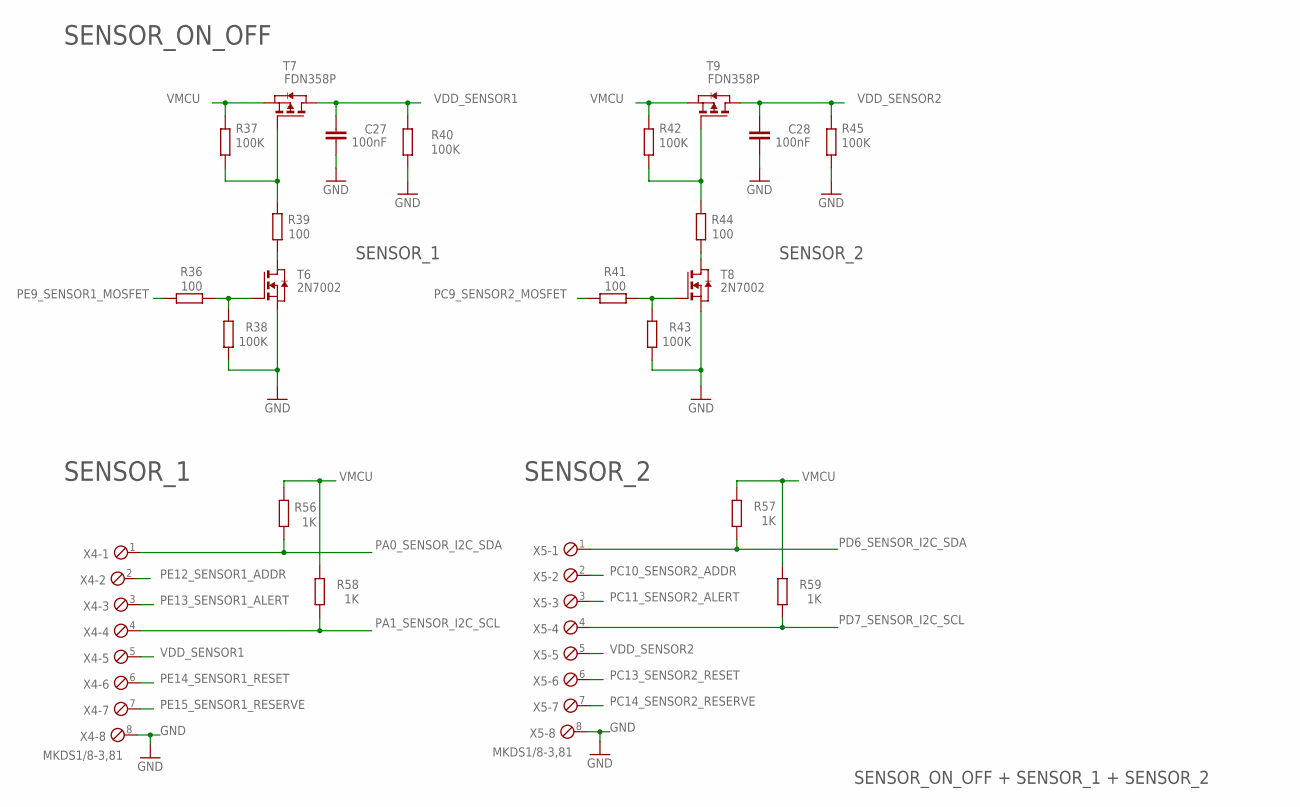
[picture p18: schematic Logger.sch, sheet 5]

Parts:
C27, C28: 100nF; C0603
R36, R39, R41, R44: 100; R0805
R37, R38, R40, R42, R43, R45: 100K; R0805
R56, R57, R58, R59: 1K; R0805
T6, T8: 2N7002; ZETEX_SOT-23
T7, T9: FDN358P; ZETEX_SOT-23
X4, X5: MKDS1/8-3,81; 8POL381

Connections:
GND: C27.2, C28.2, R38.1, R40.1, R43.1, R45.1, T6.2 (S), T8.2 (S), X4.8, X5.8; also elsewhere on the board
unnamed: R37.1, R39.2, T7.3 (G)
unnamed: R39.1, T6.1 (D)
unnamed: R36.1, R38.2, T6.3 (G)
unnamed: R42.1, R44.2, T9.3 (G)
unnamed: R44.1, T8.1 (D)
unnamed: R41.1, R43.2, T8.3 (G)
PA0_SENSOR_I2C_SDA: R56.2, X4.1; also elsewhere on the board
PA1_SENSOR_I2C_SCL: R58.1, X4.4; also elsewhere on the board
PC9_SENSOR2_MOSFET: R41.2; also elsewhere on the board
PC10_SENSOR2_ADDR: X5.2; also elsewhere on the board
PC11_SENSOR2_ALERT: X5.3; also elsewhere on the board
PC13_SENSOR2_RESET: X5.6; also elsewhere on the board
PC14_SENSOR2_RESERVE: X5.7; also elsewhere on the board
PD6_SENSOR_I2C_SDA: R57.1, X5.1; also elsewhere on the board
PD7_SENSOR_I2C_SCL: R59.1, X5.4; also elsewhere on the board
PE9_SENSOR1_MOSFET: R36.2; also elsewhere on the board
PE12_SENSOR1_ADDR: X4.2; also elsewhere on the board
PE13_SENSOR1_ALERT: X4.3; also elsewhere on the board
PE14_SENSOR1_RESET: X4.6; also elsewhere on the board
PE15_SENSOR1_RESERVE: X4.7; also elsewhere on the board
VDD_SENSOR1: C27.1, R40.2, T7.1 (D), X4.5
VDD_SENSOR2: C28.1, R45.2, T9.1 (D), X5.5
VMCU: R37.2, R42.2, R56.1, R57.2, R58.2, R59.2, T7.2 (S), T9.2 (S); also elsewhere on the board

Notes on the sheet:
SENSOR_1
SENSOR_2
SENSOR_ON_OFF
SENSOR_ON_OFF + SENSOR_1 + SENSOR_2

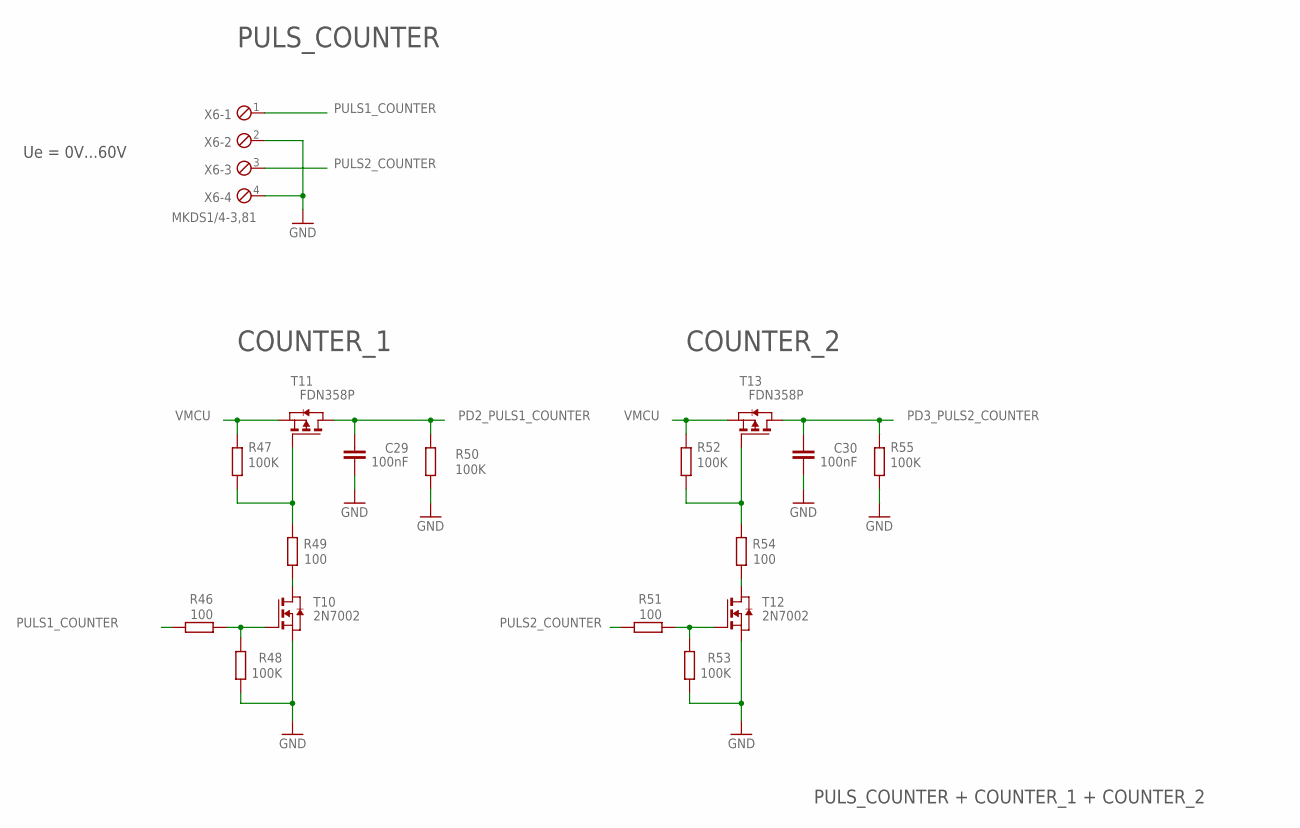
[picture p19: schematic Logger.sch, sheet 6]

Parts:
C29, C30: 100nF; C0603
R46, R49, R51, R54: 100; R0805
R47, R48, R50, R52, R53, R55: 100K; R0805
T10, T12: 2N7002; ZETEX_SOT-23
T11, T13: FDN358P; ZETEX_SOT-23
X6: MKDS1/4-3,81; 4POL381

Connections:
GND: C29.2, C30.2, R48.1, R50.1, R53.1, R55.1, T10.2 (S), T12.2 (S), X6.2, X6.4; also elsewhere on the board
unnamed: R47.1, R49.2, T11.3 (G)
unnamed: R49.1, T10.1 (D)
unnamed: R46.1, R48.2, T10.3 (G)
unnamed: R52.1, R54.2, T13.3 (G)
unnamed: R54.1, T12.1 (D)
unnamed: R51.1, R53.2, T12.3 (G)
PD2_PULS1_COUNTER: C29.1, R50.2, T11.1 (D); also elsewhere on the board
PD3_PULS2_COUNTER: C30.1, R55.2, T13.1 (D); also elsewhere on the board
PULS1_COUNTER: R46.2, X6.1
PULS2_COUNTER: R51.2, X6.3
VMCU: R47.2, R52.2, T11.2 (S), T13.2 (S); also elsewhere on the board

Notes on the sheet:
COUNTER_1
COUNTER_2
PULS_COUNTER
PULS_COUNTER + COUNTER_1 + COUNTER_2
Ue = 0V...60V

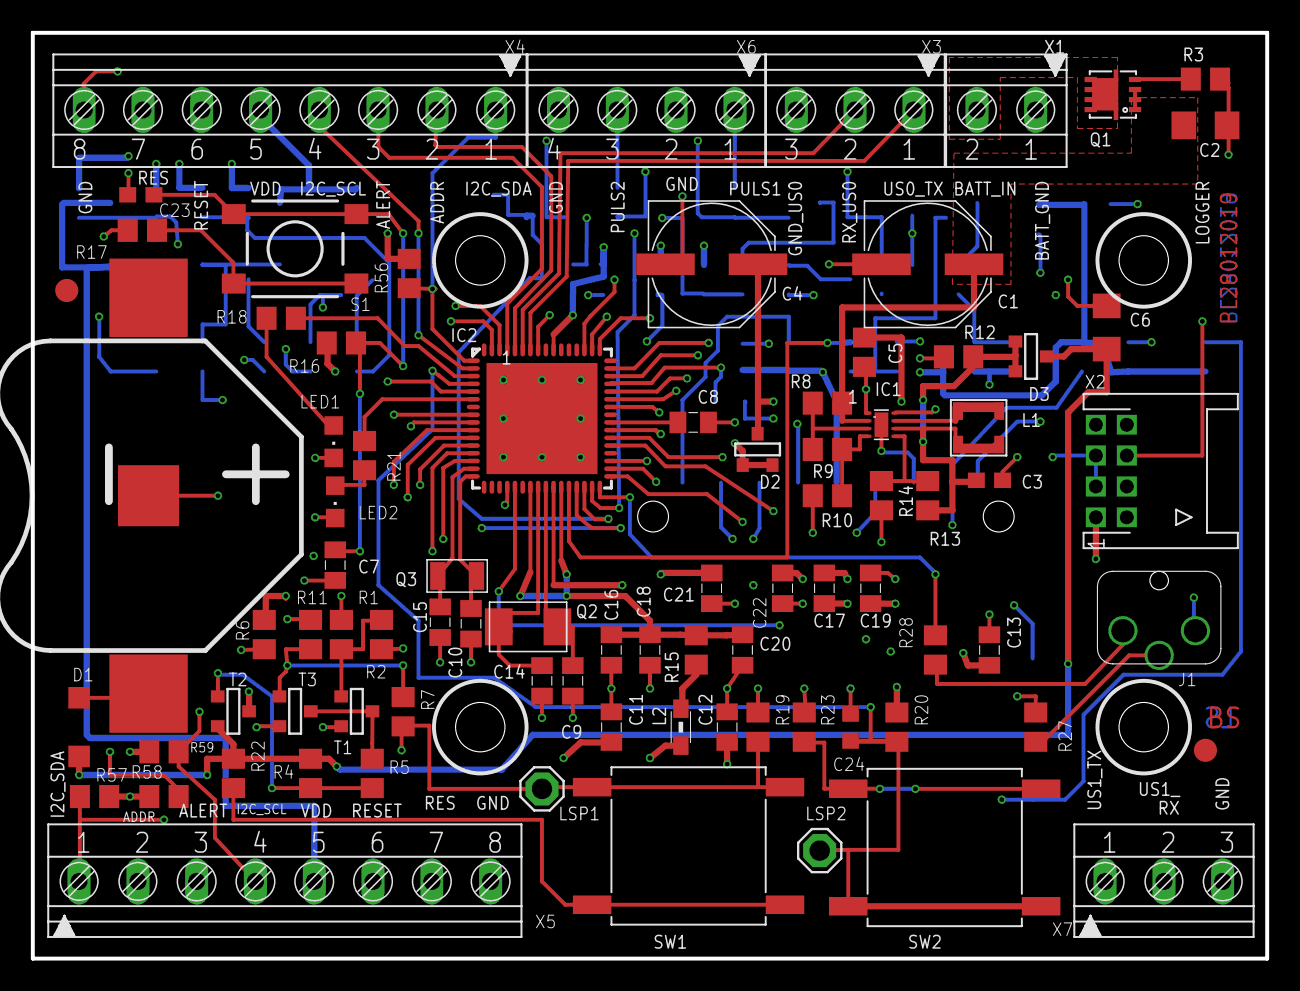
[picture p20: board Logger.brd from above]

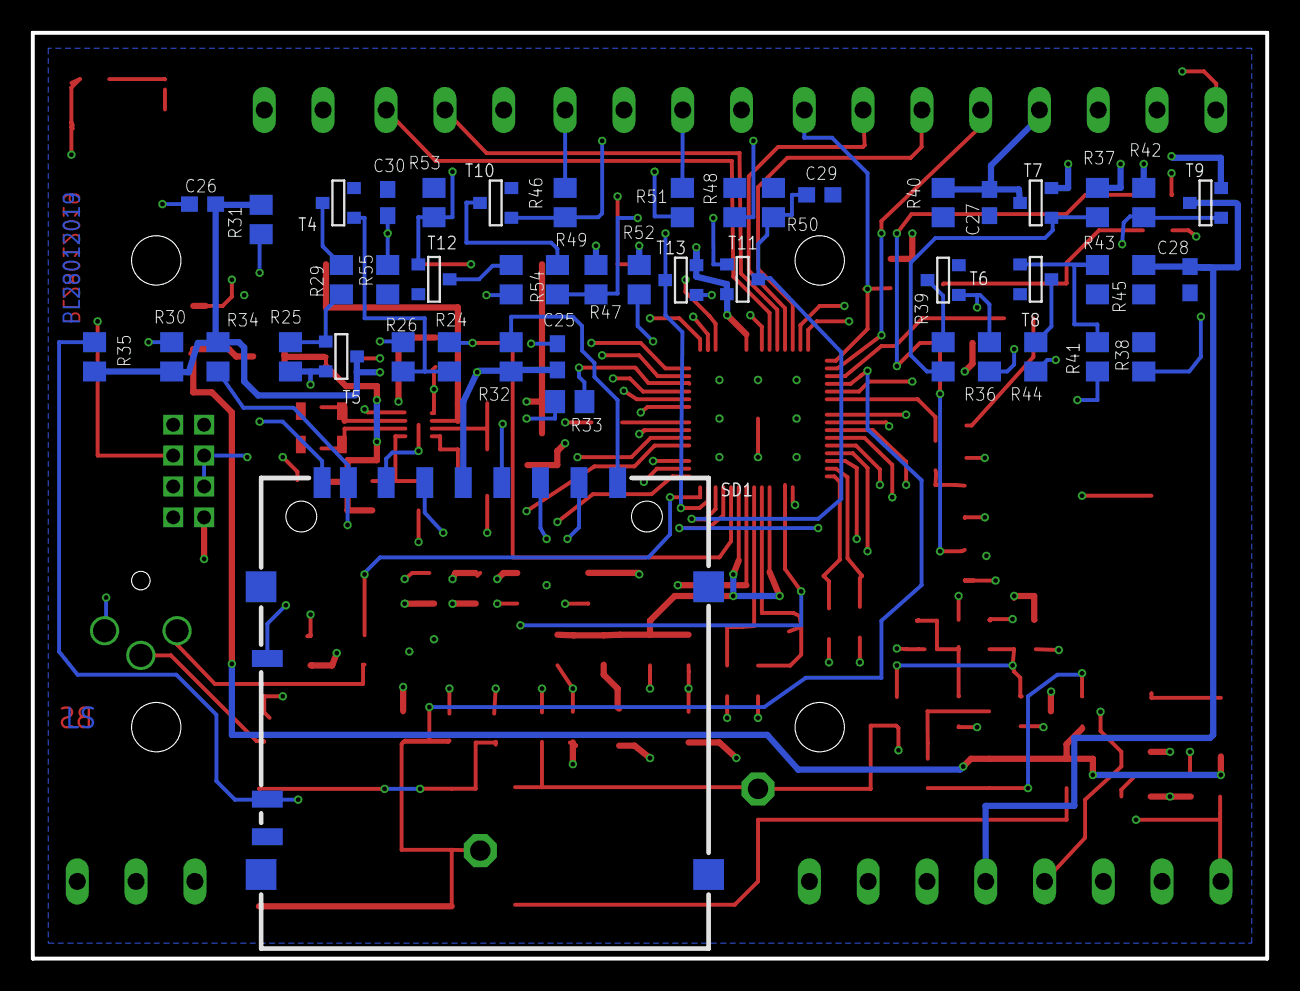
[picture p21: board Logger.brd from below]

Board: 4 copper layers, 80.0 x 60.0 mm, 131 parts (47 on the bottom side), 93 nets.

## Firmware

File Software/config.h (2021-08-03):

/***************************************************************************//**
 * @file
 * @brief	Project configuration file
 * @author	Ralf Gerhauser
 * @version	2020-05-12
 *
 * This file allows to set miscellaneous configuration parameters.  It must be
 * included by all modules.
 *
 ****************************************************************************//*
Revision History:
2020-05-12,rage	Use defines XXX_POWER_ALARM instead of ENUMs.
		Power Alarms are grouped in ON and OFF alarms now.
2016-02-26,rage	Increased LOG_BUF_SIZE to 4KB.
2016-02-10,rage	Set DFLT_RFID_POWER_OFF_TIMEOUT to 6 minutes.
2014-11-11,rage	Derived from project "AlarmClock".
*/

#ifndef __INC_config_h
#define __INC_config_h

/*=============================== Header Files ===============================*/

#include <stdio.h>
#include <stdbool.h>
#include "em_device.h"

/*=============================== Definitions ================================*/

/*
 * Basic defines
 */
    /* terminators for lists and strings */

#define	EOL		NULL		/* EndOfList		*/
#define EOS		'\0'		/* EndOfString		*/
#define	NONE		(-1)

    /* macro to calculate the number of elements of an array */
#define ELEM_CNT(array)  (sizeof (array) / sizeof ((array)[0]))

/*
 * LED Definitions for this project
 */
    /*!@brief GPIO Port of the (red) Power-LED. */
#define POWER_LED_PORT		gpioPortA
    /*!@brief GPIO Pin of the (red) Power-LED is PA2. */
#define POWER_LED_PIN		2
    /*! @brief Macro to set or clear the Power-LED */
#define POWER_LED   IO_Bit(GPIO->P[POWER_LED_PORT].DOUT, POWER_LED_PIN)
    /*!@brief GPIO Port of the (yellow) Log Flush LED. */
#define LOG_FLUSH_LED_PORT	gpioPortA
    /*!@brief GPIO Pin of the (yellow) Log Flush LED is PA5. */
#define LOG_FLUSH_LED_PIN	5		//! State: 0=OFF, 1=ON
    /*! @brief Macro to set or clear the Log Flush LED */
#define LOG_FLUSH_LED IO_Bit(GPIO->P[LOG_FLUSH_LED_PORT].DOUT, LOG_FLUSH_LED_PIN)

/*!
 * @brief MPU Clock Configuration.
 *
 * Set to 0 to use the internal RC oscillator, if 1 the external 32MHz XTAL
 * is used.  The frequency of the RC oscillator is 14MHz per default.
 */
#define USE_EXT_32MHZ_CLOCK	0

/*
 * Configuration for module "AlarmClock"
 */
    /*!@brief RTC frequency in [Hz]. */
#define RTC_COUNTS_PER_SEC	32768


/*!
 * @brief Interrupt Priority Settings
 *
 * There are 8 priority levels 0 to 7 with 0 to be the highest and 7 to be
 * the lowest priority.  ADC measurement requires high priority, otherwise
 * data gets lost.  DCF77 (which is called from the EXTI handler) and RTC
 * must use the same priority level to lock-out each other, because they
 * both use function localtime() and this is not multithreading save.
 * Funktion localtime_r() would be the right choice here, unfortunately it
 * is not available with the IAR compiler library.
 */
#define INT_PRIO_ADC	0		//!< ADC has highest priority
#define INT_PRIO_UART	2		//!< UART interrupts
#define INT_PRIO_LEUART	2		//!< LEUART RX interrupt (not used)
#define INT_PRIO_DMA	2		//!< DMA is used for LEUART
#define INT_PRIO_SMB	2		//!< SMBus used by the battery monitor
#define INT_PRIO_RTC	3		//!< lower priority than others
#define INT_PRIO_EXTI	INT_PRIO_RTC	//!< must be the same as @ref INT_PRIO_RTC

/*
 * Configuration for module Keys
 */

    /*! Enable autorepeat functionality. */
#define KEY_AUTOREPEAT	1
    /*! Time in [ms] a key needs to be asserted to start autorepeat. */
#define AUTOREPEAT_THRESHOLD	750
    /*! Rate in [ms] the autorepeat feature repeats the previous key. */
#define AUTOREPEAT_RATE		100

/*
 * Configuration for module "Logging"
 */
    /*!@brief Size of the log buffer in bytes. */
#define LOG_BUF_SIZE	4096

    /*!@brief Use this define to specify a function to be called for monitoring
     * the log activity.  Here, monitoring is done via the LEUART interface.
     */
#define LOG_MONITOR_FUNCTION	drvLEUART_puts

/* forward declaration */
void    drvLEUART_puts(const char *str);

    /*!@brief Disable "alive" message by setting this interval to 0. */
#define LOG_ALIVE_INTERVAL	0


/*!@name DMA Channel Assignment
 *
 * The following definitions assign the 8 DMA channels to the respective
 * devices or drivers.  These defines are used as index within the global
 * DMA_DESCRIPTOR_TypeDef structure @ref g_DMA_ControlBlock.
 */
//@{
#define DMA_CHAN_LEUART_RX	0	//!< LEUART Rx uses DMA channel 0
#define DMA_CHAN_LEUART_TX	1	//!< LEUART Tx uses DMA channel 1
//@}


/*================================== Macros ==================================*/

#ifdef DEBUG
    /*
     * Debugging output via ITM or LEUART
     */
    #if DEBUG_VIA_ITM
	#define DBG_PUTC(ch)	ITM_SendChar(ch)
	#define DBG_PUTS(str)	ITM_SendStr(str)
	uint32_t ITM_SendChar (uint32_t ch);
	void ITM_SendStr(const char *pStr);
    #else
	#define DBG_PUTC(ch)	drvLEUART_putc(ch)
	#define DBG_PUTS(str)	drvLEUART_puts(str)
	void	drvLEUART_putc(char ch);
	void	drvLEUART_puts(const char *str);
    #endif
    void dbgInit(void);
#else
    #define DBG_PUTC(ch)
    #define DBG_PUTS(str)
#endif

#define INCLUDE_DEBUG_TRACE 0
#if INCLUDE_DEBUG_TRACE
    #define DEBUG_TRACE(id)	DebugTrace(id)
    #define DEBUG_TRACE_STOP	DebugTraceStop()
    void DebugTrace(uint32_t id);
    void DebugTraceStop(void);
    #undef  LOG_BUF_SIZE
    #define LOG_BUF_SIZE	2048
    #define DEBUG_TRACE_COUNT	512
#else
    #define DEBUG_TRACE(id)
    #define DEBUG_TRACE_STOP
#endif

    /*! Macro to address a single bit in the I/O range (peripheral range) in
     *  an atomic manner.
     * @param address   I/O register address.
     * @param bitNum    Bit number within this register.
     */
#define IO_BIT_ADDR(address, bitNum)					\
	((__IO uint32_t *) (BITBAND_PER_BASE				\
			+ (((uint32_t)(address)) - PER_MEM_BASE) * 32	\
			+ (bitNum) * 4))

    /*! Shortcut to directly access an I/O-bit. */
#define IO_Bit(regName, bitNum)	*IO_BIT_ADDR(&regName, bitNum)

    /*! Macro to address a single bit in an SRAM variable in an atomic manner.
     * @param address   Address of the variable in SRAM.
     * @param bitNum    Bit number within this variable.
     */
#define SRAM_BIT_ADDR(address, bitNum)					\
	((__IO uint32_t *) (BITBAND_RAM_BASE				\
			+ (((uint32_t)(address)) - RAM_MEM_BASE) * 32	\
			+ (bitNum) * 4))

    /*! Shortcut to directly access a bit in a variable. */
#define Bit(varName, bitNum)	*SRAM_BIT_ADDR(&varName, bitNum)

/*=========================== Typedefs and Structs ===========================*/

/*!@brief Structure to hold Project Information */
typedef struct
{
    char const  ID[12];
    char const  Date[16];
    char const  Time[10];
    char const  Version[16];
} PRJ_INFO;


/*!@brief Enumeration of Alarm Identifiers
 *
 * This is the list of Alarm IDs used by this application.  They are used to
 * identify a particular alarm time entry via the <b>alarmNum</b> parameter
 * when calling alarm functions, e.g. AlarmSet().
 * The configurable Power Alarms must be grouped in ON and OFF alarms to be able
 * to use a single index for all, see CheckAlarmTimes() and AlarmPowerControl().
 */
typedef enum
{
    ALARM_DCF77_WAKE_UP,    //!< Wake up DCF77 to synchronize the system clock
    ALARM_BATTERY_MON_1,    //!< Time #1 for logging battery status
    ALARM_BATTERY_MON_2,    //!< Time #2 for logging battery status
 // List of programmable Alarm ON Times
    ALARM_SENSOR1_ON_TIME_1,    //!< Time #1 when to switch UA1 output ON
    ALARM_SENSOR1_ON_TIME_2,    //!< Time #2 when to switch UA1 output ON
    ALARM_SENSOR1_ON_TIME_3,    //!< Time #3 when to switch UA1 output ON
    ALARM_SENSOR1_ON_TIME_4,    //!< Time #4 when to switch UA1 output ON
    ALARM_SENSOR1_ON_TIME_5,    //!< Time #5 when to switch UA1 output ON
    ALARM_SENSOR2_ON_TIME_1,    //!< Time #1 when to switch UA2 output ON
    ALARM_SENSOR2_ON_TIME_2,    //!< Time #2 when to switch UA2 output ON
    ALARM_SENSOR2_ON_TIME_3,    //!< Time #3 when to switch UA2 output ON
    ALARM_SENSOR2_ON_TIME_4,    //!< Time #4 when to switch UA2 output ON
    ALARM_SENSOR2_ON_TIME_5,    //!< Time #5 when to switch UA2 output ON
 // List of programmable Alarm OFF Times
    ALARM_SENSOR1_OFF_TIME_1,   //!< Time #1 when to switch UA1 output OFF
    ALARM_SENSOR1_OFF_TIME_2,   //!< Time #2 when to switch UA1 output OFF
    ALARM_SENSOR1_OFF_TIME_3,   //!< Time #3 when to switch UA1 output OFF
    ALARM_SENSOR1_OFF_TIME_4,   //!< Time #4 when to switch UA1 output OFF
    ALARM_SENSOR1_OFF_TIME_5,   //!< Time #5 when to switch UA1 output OFF
    ALARM_SENSOR2_OFF_TIME_1,   //!< Time #1 when to switch UA2 output OFF
    ALARM_SENSOR2_OFF_TIME_2,   //!< Time #2 when to switch UA2 output OFF
    ALARM_SENSOR2_OFF_TIME_3,   //!< Time #3 when to switch UA2 output OFF
    ALARM_SENSOR2_OFF_TIME_4,   //!< Time #4 when to switch UA2 output OFF
    ALARM_SENSOR2_OFF_TIME_5,   //!< Time #5 when to switch UA2 output OFF
    NUM_ALARM_IDS
} ALARM_ID;

/*
 * !@brief These defines hold the first and last alarm time ENUM for Power
 * Output control, and the number of alarm ON, resp. OFF times.
 */
//@{
#define FIRST_POWER_ALARM	ALARM_SENSOR1_ON_TIME_1
#define LAST_POWER_ALARM	ALARM_SENSOR2_OFF_TIME_5
#define NUM_POWER_ALARMS	(LAST_POWER_ALARM - ALARM_SENSOR1_OFF_TIME_1 + 1)
//@}


/*
 * !@brief The following defines set the first on and off alarm, and the number
 * of alarm time entries of a specific power output.
 */
//@{
#define FIRST_ALARM_ON_TIME	ALARM_SENSOR1_ON_TIME_1
#define FIRST_ALARM_OFF_TIME	ALARM_SENSOR1_OFF_TIME_1
#define NUM_ALARM_UA1		5
#define NUM_ALARM_UA2		5
//@}


/*!@brief Enumeration of the EM1 Modules
 *
 * This is the list of Software Modules that require EM1 to work, i.e. they
 * will not work in EM2 because clocks, etc. would be disabled.  These enums
 * are used to set/clear the appropriate bit in the @ref g_EM1_ModuleMask.
 */
typedef enum
{
    EM1_MOD_ADC,	//!<  1: ADC is a HFPER clock device
    END_EM1_MODULES
} EM1_MODULES;

/*======================== External Data and Routines ========================*/

extern volatile bool	 g_flgIRQ;		// Flag: Interrupt occurred
extern volatile uint16_t g_EM1_ModuleMask;	// Modules that require EM1


#endif /* __INC_config_h */

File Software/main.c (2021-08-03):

/***************************************************************************//**
 * @file
 * @brief	SL Sensor_Logger
 * @author	Peter Loes
 * @version	2021-06-21
 *
 * This application consists of the following modules:
 * - main.c - Initialization code and main execution loop.
 * - DMA_ControlBlock.c - Control structures for the DMA channels.
 * - Control.c - Sequence Control module.
 * - CfgData.c - Handling of configuration data.
 * - ExtInt.c - External interrupt handler.
 * - Keys.c - Key interrupt handling and translation.
 * - AlarmClock.c - Alarm clock and timers facility.
 * - clock.c - An implementation of the POSIX time() function.
 * - LEUART.c - The Low-Energy UART can be used as monitoring and debugging
 *   connection to a host computer.
 * - microsd.c - Together with the files "diskio.c" and "ff.c", this module
 *   provides an implementation of a FAT file system on the @ref SD_Card.
 * - Logging.c - Logging facility to send messages to the LEUART and store
 *   them into a file on the SD-Card.
 * - Update.c - Hold PowerUp the Device. Manage KeyHandler.
 *   Update Data Logger functions.     
 * - SensorMon.c - Sensor monitor, allows to read the state of the
 *   sensor via the SMBus.
 *
 * Parts of the code are based on the example code of AN0006 "tickless calender"
 * and AN0019 "eeprom_emulation" from Energy Micro AS.
 *
 ***************************************************************************//**
 *
 * Parts are Copyright 2013 Energy Micro AS, http://www.energymicro.com
 *
 *******************************************************************************
 *
 * Permission is granted to anyone to use this software for any purpose,
 * including commercial applications, and to alter it and redistribute it
 * freely, subject to the following restrictions:
 *
 * 1. The origin of this software must not be misrepresented; you must not
 *    claim that you wrote the original software.
 * 2. Altered source versions must be plainly marked as such, and must not be
 *    misrepresented as being the original software.
 * 3. This notice may not be removed or altered from any source distribution.
 * 4. The source and compiled code may only be used on Energy Micro "EFM32"
 *    microcontrollers and "EFR4" radios.
 *
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
 * Energy Micro AS will not be liable for any consequential, incidental, or
 * special damages, or any other relief, or for any claim by any third party,
 * arising from your use of this Software.
 *
 ****************************************************************************//*
Revision History:
2021-06-11,rage	Call CheckAlarmTimes() after CONFIG.TXT has been read.
2021-06-11,rage	Moved DMA related variables to module "DMA_ControlBlock.c".
		Calling VerifyConfiguration() ensures data is valid.
2021-06-07,rage	Initial version.
*/
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

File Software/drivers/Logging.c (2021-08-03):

/***************************************************************************//**
 * @file
 * @brief	Logging
 * @author	Ralf Gerhauser
 * @version	2018-03-16
 *
 * This module provides a logging facility to send messages to the LEUART and
 * store them into a file on the SD-Card.
 *
 ****************************************************************************//*
Revision History:
2018-03-16,rage	Disable interrupts for a minimum of time to prevent data loss
		of the ADC interrupt handler.
		The Log Flush LED is no more flashing (just lights), because
		the msTimer is used for the Key repeat functionality.
		Added LogFlushTrigger() to force a flush from another module.
2016-09-27,rage	LogFlushCheck: Flush log buffer if threshold has been reached,
		even if LOG_FLUSH_PAUSE is not over.
		Print logging timestamp with milliseconds resolution.
		Use INT_En/Disable() instead of __en/disable_irq().
2015-07-09,rage	IAR Compiler: Use sprintf() instead siprintf().
2015-04-02,rage	Initial version.
*/

/*=============================== Header Files ===============================*/

#include <stdio.h>
#include <stdarg.h>
#include <string.h>
#include "em_device.h"
#include "em_assert.h"
#include "em_int.h"
#include "AlarmClock.h"
#include "Logging.h"
#include "ff.h"		// FS_FAT12/16/32
#include "diskio.h"	// DSTATUS
#include "microsd.h"

/*=============================== Definitions ================================*/

#if LOG_MONITOR_FUNCTION == NONE
    #undef LOG_MONITOR_FUNCTION
#endif


    /*!@name Hardware Configuration: Log Flush LED. */
//@{
    /*! Get or set level of the Log Flush LED */
#define LOG_FLUSH_LED  IO_Bit(GPIO->P[LOG_FLUSH_LED_PORT].DOUT, LOG_FLUSH_LED_PIN)
#if KEY_AUTOREPEAT	// ms-Timer is already in use
  #define LOG_FLASH_LED_DURATION 2	// Duration [s] how long the LED is on
#else
  #define LOG_FLASH_LED_DELAY	50	// Delay [ms] between toggling the LED
  #define LOG_FLASH_LED_CNT	5	// How often the LED is flashing
#endif
//@}
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

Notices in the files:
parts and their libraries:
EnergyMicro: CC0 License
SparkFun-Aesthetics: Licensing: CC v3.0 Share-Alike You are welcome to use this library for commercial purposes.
